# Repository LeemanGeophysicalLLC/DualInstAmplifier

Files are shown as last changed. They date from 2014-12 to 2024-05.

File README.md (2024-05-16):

# Dual Channel Instrumentation Amplifier

**THIS PRODUCT HAS BEEN RETIRED AND IS NO LONGER PRODUCED**

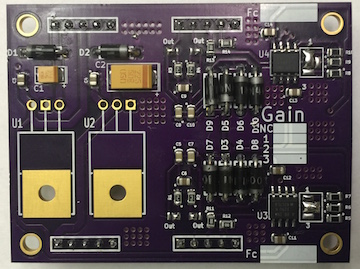
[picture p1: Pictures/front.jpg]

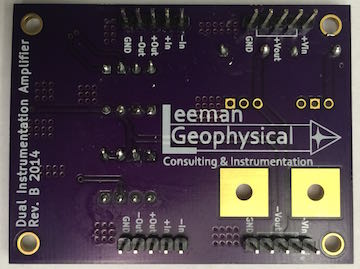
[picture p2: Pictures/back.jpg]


## Purpose

To provide an easy way to buffer, amplify, and filter analog signals. This is a
common problem in prototyping and laboratory settings where instrumentation is
often tested, changed, reconfigured, etc. This instrumentation grade product is
built around the INA128 amplifier.

## Purchasing

The dual channel instrumentation amplifier is available through Leeman
Geophysical by emailing [John R. Leeman](http://www.johnrleeman.com) at
<kd5wxb@gmail.com>.

## Project Information

This repository includes all design information, CAD files, PDF CAD output,
gerbers, etc.

Additional resources for this project include:

- [Bill of Materials](BoM.md) (BoM)
- [INA128 Datasheet](PDFs/ina128.pdf)

## License

This product is licenced under the CERN Open Hardware License 1.2. The [full
license](cern_ohl_v_1_2.txt) is included in this repository.

## Hookup Guide

Hookup is self-explanitory, but some basic guidelines and cautions
are provided below.

- Apply power and ground to the GND, Vin+, and Vin- terminals. The input voltage
should follow the specifications for the voltage regulators fitted on your
device. Normally 2-3 V over the regualted voltage is ideal.

- Apply signal to the In+ and In- terminals

- Hookup the output to your device (recorder, process, etc) via the Out+ and
Out- terminals

- Note: Regulated power is available, but be mindful of the current pulled by
sensors to not exceed the ratings of the on-board voltage regulators.

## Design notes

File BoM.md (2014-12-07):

# Bill of Materials

| Quantity | P/N           | Description                     | Supplier |
|----------|---------------|---------------------------------|----------|
| 1        | 399-3779-1-ND | CAP TANT 2.2UF 50V 10% 2917     | Digi-Key |
| 1        | 399-3718-1-ND | CAP TANT 0.33UF 50V 20% 1411    | Digi-Key |
| 1        | LM7815CTFS-ND | IC REG LDO 15V 1A TO220-3       | Digi-Key |
| 1        | LM7915CTFS-ND | IC REG LDO -15V 1A TO220-3      | Digi-Key |
| 10       | 641-1310-1-ND | DIODE GEN PURPOSE 50V 1A DO41   | Digi-Key |
| 8        | P0.0ACT-ND    | RES 0.0 OHM 1/8W JUMP 0805 SMD  | Digi-Key |
| 8        | 399-7409-1-ND | CAP CER 1UF 50V 10% X7R 0805    | Digi-Key |
| 2        | INA128UA-ND   | IC OPAMP INSTR 1.3MHZ 8SOIC     | Digi-Key |
| 4        | P154DACT-ND   | RES 154 OHM 1/8W .1% 0805 SMD   | Digi-Key |
| 2        | P5.62KDACT-ND | RES 5.62K OHM 1/8W .1% 0805 SMD | Digi-Key |
| 4        | 399-1170-1-ND | CAP CER 0.1UF 50V 10% X7R 0805  | Digi-Key |
| 2        | P511DACT-ND   | RES 511 OHM 1/8W .1% 0805 SMD   | Digi-Key |
| 2        | P49.9KDACT-ND | RES 49.9K OHM 1/8W .1% 0805 SMD | Digi-Key |

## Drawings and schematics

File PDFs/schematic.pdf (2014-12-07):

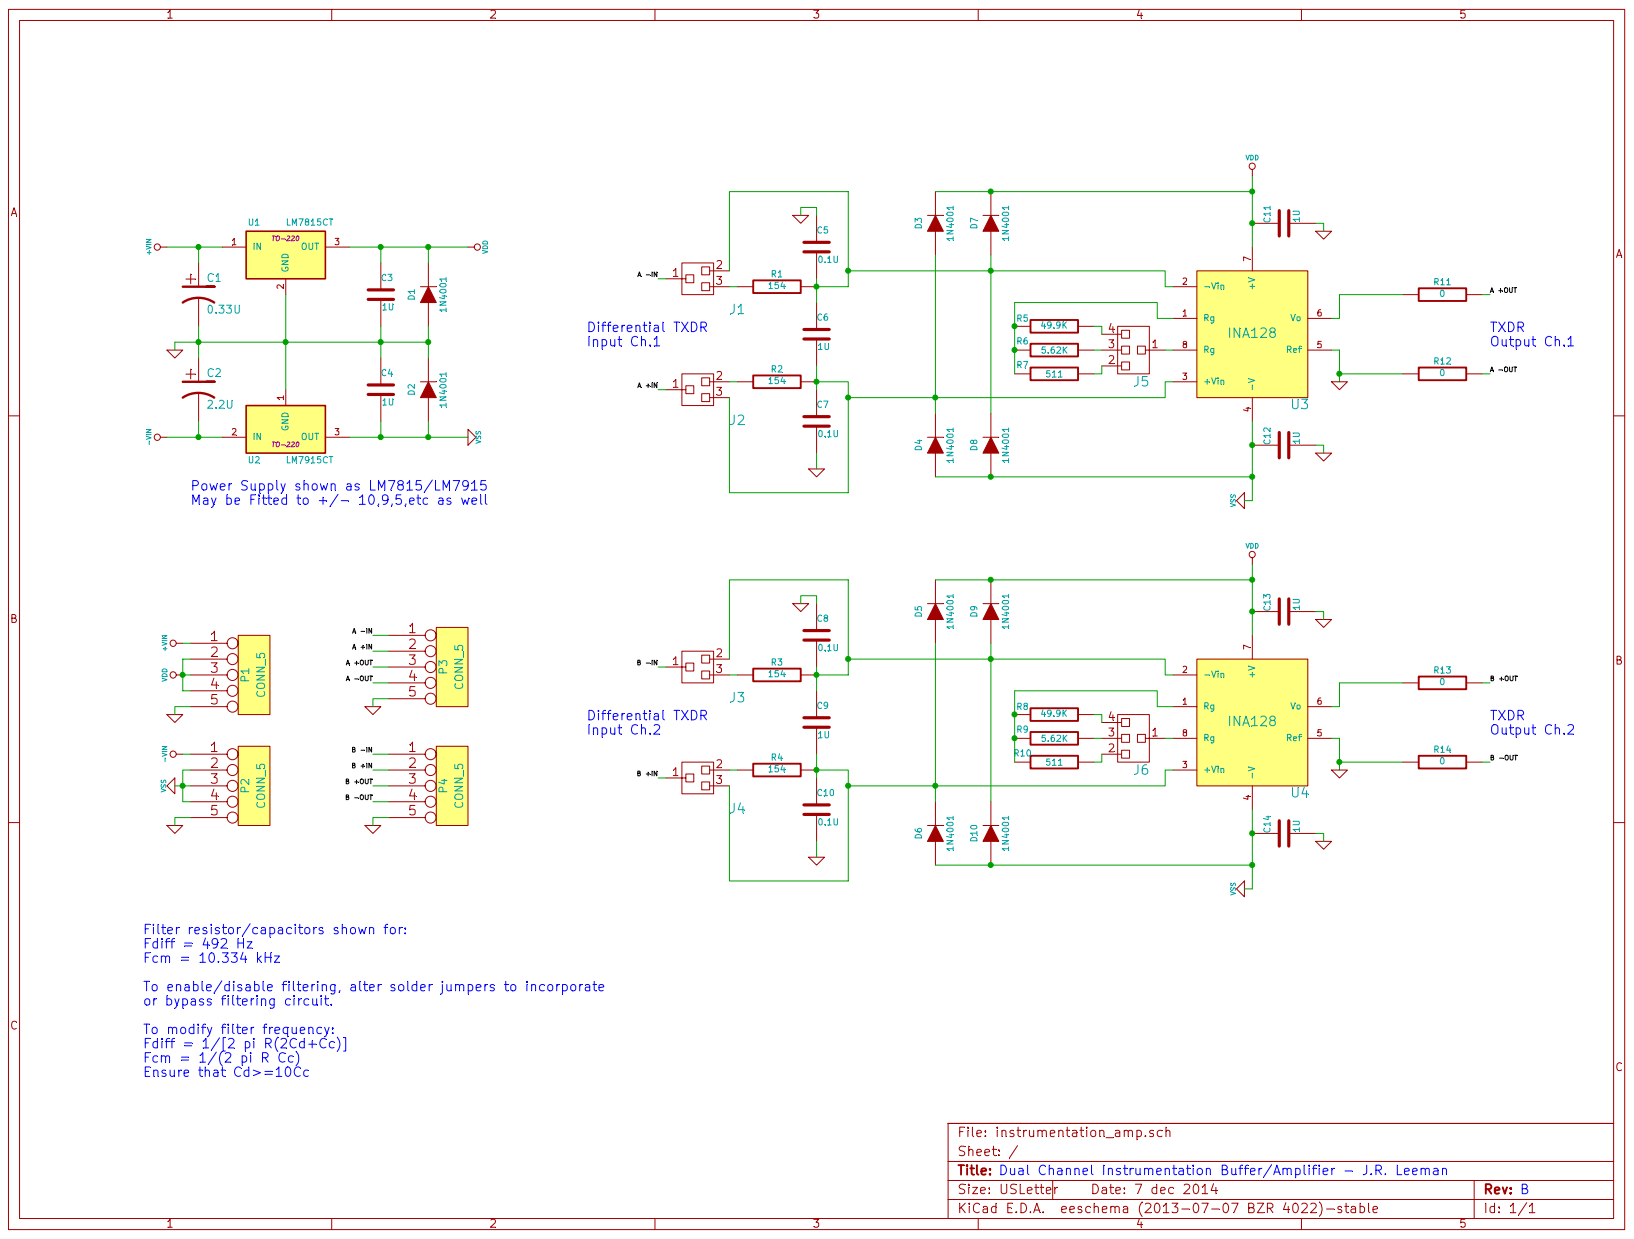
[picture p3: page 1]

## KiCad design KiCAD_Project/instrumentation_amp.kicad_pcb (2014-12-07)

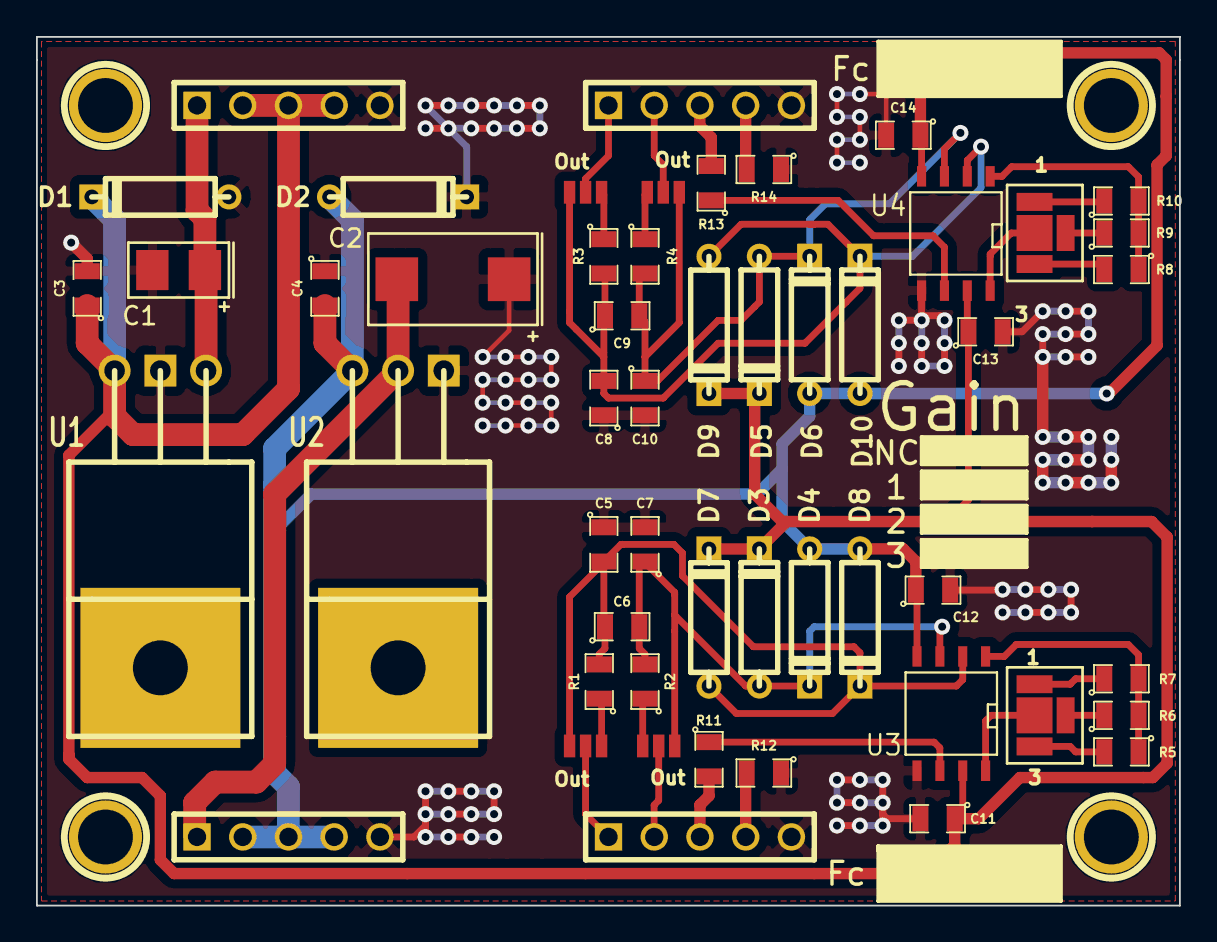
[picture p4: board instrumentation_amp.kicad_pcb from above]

Board: 2 copper layers, 63.5 x 48.3 mm, 56 parts (0 on the bottom side), 33 nets.

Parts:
1PIN, 1PIN#2, 1PIN#3, 1PIN#4: P***; 1pin
C1: 0.33U; C1411Pol
C2: 2.2U; C2917Pol
C3, C4, C6, C9, C11, C12, C13, C14: 1U; SM0805
C5, C7, C8, C10: 0.1U; SM0805
D1, D2, D3, D4, D5, D6, D7, D8, D9, D10: 1N4001; D3
J1, J2, J3, J4: SPDT_SOLDER; SPDT
J5, J6: SP3T_SOLDER; Solder_SPTT
P1, P2, P3, P4: CONN_5; PIN_ARRAY_5x1
R1, R2, R3, R4: 154; SM0805
R5, R8: 49.9K; SM0805
R6, R9: 5.62K; SM0805
R7, R10: 511; SM0805
R11, R12, R13, R14: 0; SM0805
U1: LM7815CT; LM78XX_Numbered
U2: LM7915CT; LM79XX_Numbered
U3, U4: INA128; SO8N

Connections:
+Vin: C1.1, P1.1, U1.1
-Vin: C2.2, P2.1, U2.2
/A +IN: J2.1, P3.2
/A +OUT: P3.3, R11.2
/A -IN: J1.1, P3.1
/A -OUT: P3.4, R12.2
/B +IN: J4.1, P4.2
/B +OUT: P4.3, R13.2
/B -IN: J3.1, P4.1
/B -OUT: P4.4, R14.2
GND: C1.2, C2.1, C3.2, C4.1, C5.1, C7.2, C8.1, C10.2, C11.2, C12.2, C13.2, C14.2, D1.1, D2.2, P1.5, P2.5, P3.5, P4.5, R12.1, R14.1, U1.2, U2.1, U3.5, U4.5
unnamed: J4.2, R4.1
unnamed: J3.3, R3.1
unnamed: J6.4, R8.2
unnamed: C8.2, C9.1, D9.1, D10.2, J3.2, R3.2, U4.2
unnamed: C9.2, C10.1, D5.1, D6.2, J4.3, R4.2, U4.3
unnamed: R13.1, U4.6
unnamed: J6.2, R10.1
unnamed: J6.3, R9.1
unnamed: J6.1, U4.8
unnamed: R11.1, U3.6
unnamed: C6.2, C7.1, D3.1, D4.2, J2.3, R2.2, U3.3
unnamed: J5.1, U3.8
unnamed: C5.2, C6.1, D7.1, D8.2, J1.2, R1.2, U3.2
unnamed: R8.1, R9.2, R10.2, U4.1
unnamed: J5.3, R6.1
unnamed: J5.2, R7.1
unnamed: R5.1, R6.2, R7.2, U3.1
unnamed: J5.4, R5.2
unnamed: J1.3, R1.1
unnamed: J2.2, R2.1
VDD: C3.1, C11.1, C13.1, D1.2, D3.2, D5.2, D7.2, D9.2, P1.2, P1.3, P1.4, U1.3, U3.7, U4.7
VSS: C4.2, C12.1, C14.1, D2.1, D4.1, D6.1, D8.1, D10.1, P2.2, P2.3, P2.4, U2.3, U3.4, U4.4

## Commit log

2014-12-07 Initial commit - Rev.A
    [BOM.xlsx, instrumentation_amp-B_Cu.gbl, instrumentation_amp-B_Mask.gbs, instrumentation_amp-B_SilkS.gbo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]
2014-12-07 Change jumpers for better operation and rework the layout
    [instrumentation_amp.kicad_pcb, instrumentation_amp.sch]
2014-12-07 Final changes for Rev.B of PCB
    [instrumentation_amp-B_Cu.gbl, instrumentation_amp-B_Mask.gbs, instrumentation_amp-B_SilkS.gbo, instrumentation_amp-Edge_Cuts.gbr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]
2014-12-07 Improve readme and move BoM to plain text markdown
    [BOM.xlsx]
2014-12-07 Add solder paste stencil files
    [instrumentation_amp-Edge_Cuts.gbr, instrumentation_amp-F_Mask.gts, instrumentation_amp.sch]
2014-12-08 Fix stencil layer problem
    [instrumentation_amp-Edge_Cuts.gbr, instrumentation_amp-F_Paste.gtp]
2014-12-08 Add photos of device
